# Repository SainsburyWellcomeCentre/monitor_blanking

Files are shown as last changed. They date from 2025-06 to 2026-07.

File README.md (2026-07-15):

# Monitor Blanking

A TTL-controlled light switch designed to blank monitor displays for use in behavioural experiments.

> **Note:** This device modifies existing monitors. Some tuning may be required depending on the model.

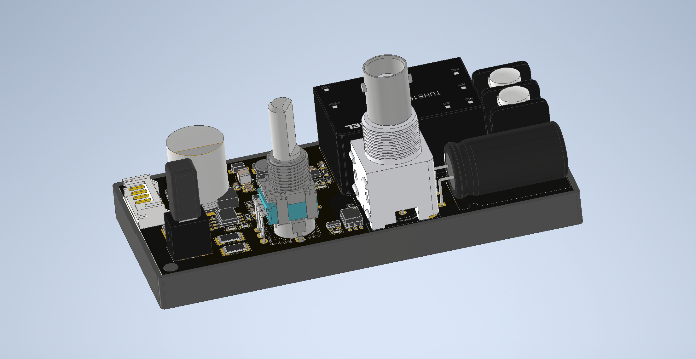
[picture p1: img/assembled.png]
Assembled


In systems neuroscience research, you want to present visual stimuli to animals without damaging the sensors you use to record neural activity. e.g. photomultiplier (PMT) for multiphoton imaging. Monitor blanking is a commonly used approach to minimize monitor light contamination by blanking the monitor backlight during the imaging pixel acquisition. The monitor turns on only during flyback periods of the fast-scan axis. Another approach is to use [a 3D-printed cone](https://labrigger.com/blog/2024/11/17/a-fantastic-shroud-for-visual-stimulation-during-imaging/).

## 🔧 Features

- Electrically isolated TTL input (up to 1 MHz)
- Sub-1 µs switching time
- Adjustable backlight brightness
- Forced-on switch for testing/debugging
- Supports up to 15 W output power

## 🌐 View Online (eCAD)

View the complete electronic design project online via [Altium 365 Viewer](https://sainsburywellcomecentre.github.io/fablabs-documentation/#fablabs-monitor-blanking).



## Build your own

Check out the **[latest release](https://github.com/SainsburyWellcomeCentre/fablabs-monitor-blanking/releases/latest)** for complete production files and instructions to build your own monitor blanking circuit.

## 🚀 Getting Started

Connect the monitor to your computer and adjust the resolution, scaling, etc. On Windows, navigate to `Settings > System > Display`. Pressing the **Forced ON** button will enable _debug_ mode, where the monitor functions as a standard monitor without digital pulses.

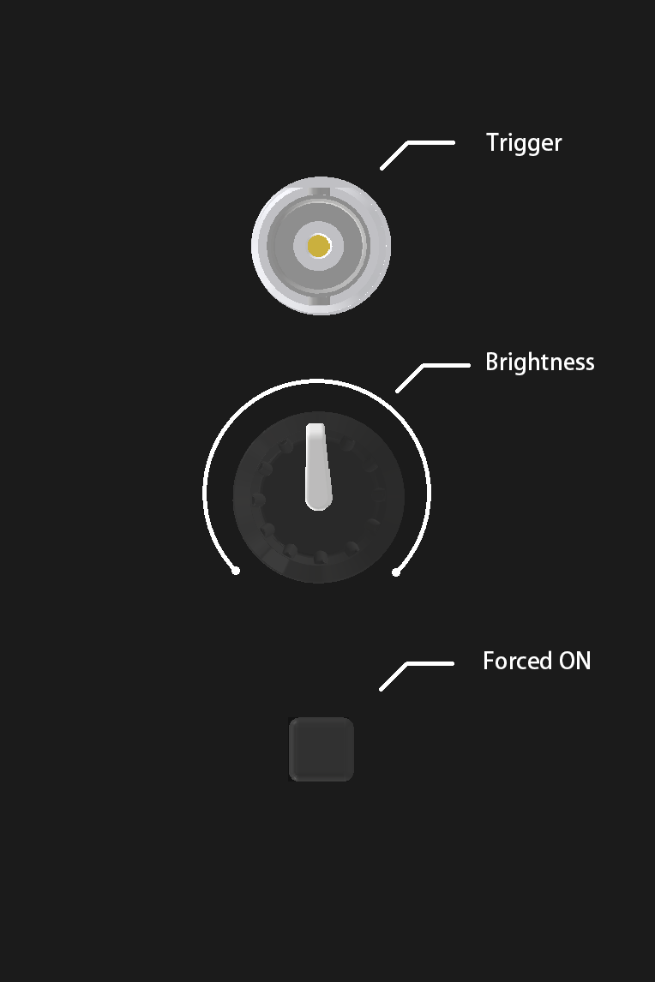
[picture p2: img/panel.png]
Panel


Once the monitor is detected and configured (also disable the _debug_ mode), send digital pulses from your fast-axis mirror through the **Trigger** BNC connection. A low signal will blank the monitor, and a high signal will allow backlight illumination. (hence, you cannot see anything if you are not sending TTL pulses.) Here are example functions for ScanImage users to generate and send monitor blanking TTLs. [BaselLaserMouse/ScanImageTools](https://github.com/BaselLaserMouse/ScanImageTools)

The luminance of the monitor can be measured using a luminance meter (e.g. LS-100, Konica Minolta) or a light sensor (e.g. Photodiode, Champalimaud Foundations’s Hardware Platform).

## ⚙️ Fine-Tuning the Blanking Driver

The blanking driver circuit is designed to support a wide range of monitor backlight types. However, to ensure optimal performance, you may need to fine-tune the **VLED** voltage.

### 🔧 Voltage Adjustment Guidelines

- Press the pushbutton to force the monitor **ON**, then use the trimmer **R9** to adjust the **VLED** until the backlight reaches the desired brightness level.
- The output voltage **VLED** can be adjusted within the range of **41 V to 61 V**.
  > The recommended **VLED** is at least **2 V higher** than the forward voltage of the backlight panel.

<div align="center">
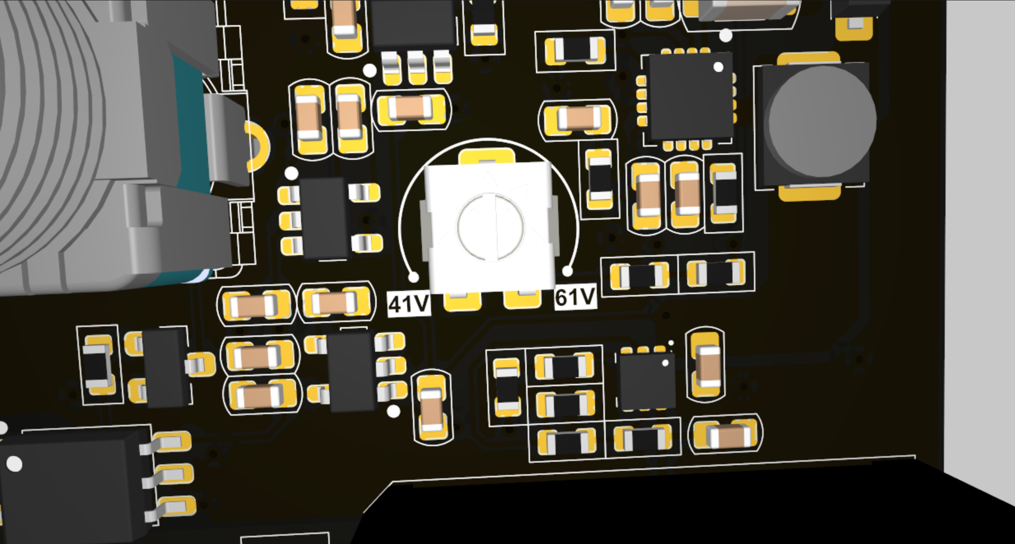
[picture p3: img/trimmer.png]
Trimmer R9
  
</div>

## 💻 Software Requirements

To access the source CAD projects:

- **Altium Designer 24** or newer  
  Academic licenses available via [Altium Education](https://www.altium.com/education/)
- **Autodesk Inventor Pro 2025** or newer  
  Academic licenses via [Autodesk Education](https://www.autodesk.com/education/home)

## 📜 License

**Sainsbury Wellcome Centre hardware is released under** [Creative Commons Attribution-ShareAlike 4.0 International](http://creativecommons.org/licenses/by-sa/4.0/).

You are free to:

- **Share** — copy and redistribute the material in any medium or format
- **Adapt** — remix, transform, and build upon the material for any purpose

Under the following terms:

- **Attribution** — Give appropriate credit, link to the license, and indicate changes.
- **ShareAlike** — Distribute your contributions under the same license.
- **No additional restrictions** — Don’t apply legal or technological measures that prevent others from doing anything the license permits.

> For the full legal text, see [LICENSE](LICENSE).

## 📚 Reference

```bibtex
@ARTICLE{Leinweber2014-nf,
  title     = "Two-photon calcium imaging in mice navigating a virtual reality environment",
  author    = "Leinweber, Marcus and Zmarz, Pawel and Buchmann, Peter and Argast, Paul and Hübener, Mark and Bonhoeffer, Tobias and Keller, Georg B",
  journal   = "Journal of visualized experiments: JoVE",
  number    =  84,
  pages     = "e50885",
  month     =  feb,
  year      =  2014,
  url       =  "https://app.jove.com/t/50885/two-photon-calcium-imaging-mice-navigating-virtual-reality",
  doi       =  {10.3791/50885}
}

```

## 🤝 Contributing

1. Fork the repository
2. Create a feature branch
3. Make your changes
4. Submit a pull request

## ❤ Contributors

 <a href = "https://github.com/sainsburywellcomecentre/fablabs-monitor-blanking/graphs/contributors">
   Contributors
 </a>

## 📧 Contact

- **Author**: [Sainsbury Wellcome Centre FabLabs](https://www.sainsburywellcome.org/content/fablab)
- **Email**: [swc.fablabs@ucl.ac.uk](mailto:swc.fablabs@ucl.ac.uk)
- **Website**: [FabLabs](https://sainsburywellcomecentre.github.io/fablabs-documentation/#fablabs-monitor-blanking)

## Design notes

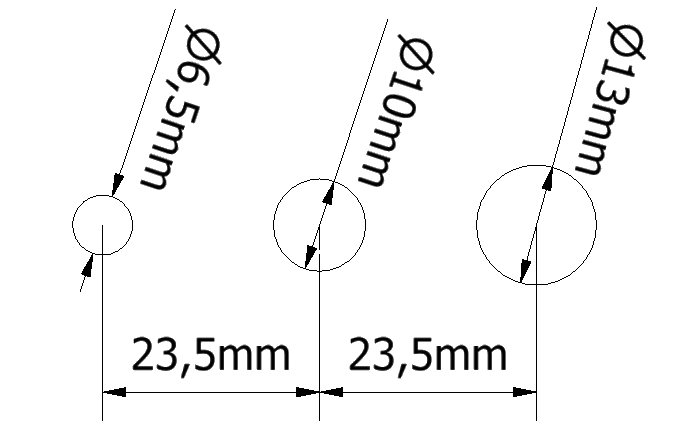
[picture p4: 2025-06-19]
img/drill.png

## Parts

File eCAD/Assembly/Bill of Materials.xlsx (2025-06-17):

Designator | Quantity | Value | PartNumber | Comment | Description | Footprint | LCSC Part N.
R9 | 1 | 1k | 3314J-1-102E | VR-SMD-1K-B | Trimmer, Cermet, 0.25W, 1000ohm, 300V, 20% +/-Tol, -100,100ppm/Cel, 1 Turn(s), 2018 | VR_SMD_4.5mm | C124640
U1 | 1 |  | TUHS15F12 | TUHS15F12 | AC/DC 15W 12V Single Output Power Supply, Encapsulated Board Mount Module | TUHS15F12 | C3031238
U7 | 1 |  | TPS70933DBVR | TPS70933 | LDO Regulator Pos 3.3V 0.15A 5-Pin SOT-23 T/R | SOT23-5 | C89347
U6 | 1 |  | TPS60403DBVR | TPS60403 | 60mA Charge Pump Voltage Inverter with Fixed 250kHz Operation 5-SOT-23 -40 to 85 | SOT23-5 | C11338
U4 | 1 |  | TPS25961DRVR | TPS25961 | 2.7-V–19-V, 106-mΩ, eFuse With Adjustable Current Limit and Short-Circuit | WSON6 | C5571272
U2 | 1 |  | TLP2361(TPL,E(T | TLP2361 | Logic IC Output Optocoupler, 1-Channel, 1-Element, 3750V Isolation, 20MBps | SO5 | C107626
U5 | 1 |  | SPX3819M5-L | SPX3819-ADJ | Adjustable Positive LDO Regulator, 0.7V Dropout, PDSO5 | SOT23-5 | C9056
R1 | 1 | 47R | RC2010FK-0747RL | R2010-47R | Res Thick Film 2010 47 Ohm 1% 3/4W ±100ppm/°C Molded SMD SMD Embossed T/R | RES_CHIP_2010 | C877463
R21 | 1 | 200mR | WSL2010R2000FEA18 | R2010-0R2 | Res Metal Strip 2010 0.2 Ohm 1% 1W ±75ppm/°C Molded SMD SMD Embossed Plastic T/R | RES_CHIP_2010 | C2073579
R4 | 1 | 470 | 0603WAF4700T5E | R0603-470R | 100mW Thick Film Resistors 75V ±100ppm/℃ ±1% 0603 Chip Resistor | RES_CHIP_0603 | C23179
R11 | 1 | 470k | 0603WAF4703T5E | R0603-470K | 100mW Thick Film Resistors 75V ±100ppm/℃ ±1% 0603 Chip Resistor | RES_CHIP_0603 | C23178
R16 | 1 | 390k | 0603WAF3903T5E | R0603-390K | 100mW Thick Film Resistors 75V ±100ppm/℃ ±1% 0603 Chip Resistor | RES_CHIP_0603 | C23150
R22 | 1 | 240k | AC0603DR-07240KL | R0603-240K | 100mW Thick Film Resistors 75V ±100ppm/℃ ±1% 0603 Chip Resistor | RES_CHIP_0603 | C227471
R5 | 1 | 120k | 0603WAF1203T5E | R0603-120K | 100mW Thick Film Resistors 75V ±100ppm/℃ ±1% 0603 Chip Resistor | RES_CHIP_0603 | C25808
R7 | 1 | 100k | 0603WAF1003T5E | R0603-100K | 100mW Thick Film Resistors 75V ±100ppm/℃ ±1% 0603 Chip Resistor | RES_CHIP_0603 | C25803
R15, R17 | 2 | 47k | 0603WAF4702T5E | R0603-47K | 100mW Thick Film Resistors 75V ±100ppm/℃ ±1% 0603 Chip Resistor | RES_CHIP_0603 | C25819
R12 | 1 | 39k | 0603WAF3902T5E | R0603-39K | 100mW Thick Film Resistors 75V ±100ppm/℃ ±1% 0603 Chip Resistor | RES_CHIP_0603 | C23153
R2, R8, R13, R23 | 4 | 10k | 0603WAF1002T5E | R0603-10K | 100mW Thick Film Resistors 75V ±100ppm/℃ ±1% 0603 Chip Resistor | RES_CHIP_0603 | C25804
R14 | 1 | 2.2k | 0603WAF2201T5E | R0603-2K2 | 100mW Thick Film Resistors 75V ±100ppm/℃ ±1% 0603 Chip Resistor | RES_CHIP_0603 | C4190
R6 | 1 | 2k | 0603WAF2001T5E | R0603-2K | 100mW Thick Film Resistors 75V ±100ppm/℃ ±1% 0603 Chip Resistor | RES_CHIP_0603 | C22975
R10, R18, R19, R20 | 4 | 1k | 0603WAF1001T5E | R0603-1K | 100mW Thick Film Resistors 75V ±100ppm/℃ ±1% 0603 Chip Resistor | RES_CHIP_0603 | C21190
D1 | 1 |  | PMEG10010ELRX | PMEG10010ELR | On a Reel of 3000, Nexperia 100V 1.4A, Schottky Diode, 2-Pin SOD-123W PMEG10010ELRX | SOD123 | C179426
U8 | 1 |  | OPA2197IDR | OPA2197 | 10MHz 5pA Dual channel SOIC-8 Precision Op Amps | SOIC8 | C139363
L1 | 1 | 10uH | SPM4015T-100M-LR | L-PWR-10uH-1.5A | Inductor Power Shielded Wirewound 10uH 20% 100KHz Metal 1.5A 0.345Ohm DCR T/R | IND_PWR_0404 | C695172
U3 | 1 |  | LM5158QRTERQ1 | LM5158 | 5-A, 40-V, wide VIN boost, flyback, & SEPIC converter 16-WQFN -40 to 150 | QFN16_3X3_0.5E_EP | C3188431
CN3 | 1 |  | 5227222-3 | LIGHT TRIGGER | RF BNC Connector, Female, Panel Mount, Board Mount, Solder Terminal, Jack | BNC-TE-5227222 | C3175614
SW1 | 1 |  | SPPH410100 | FORCE ON | Switch Push Button N.O./N.C. DPDT Plunger 0.1A 30VDC Latching PC Pins Thru-Hole Bulk | SW_LOCK_SPPH410100 | C370973
C3 | 1 | 220uF | EEEFK1J221AQ | EC125-220uF-63V | Radial Can - SMD ALUMINUM ELECTROLYTIC CAPACITOR FK 63V 220muF 20% 0.492Dia 12.50mm | ECAP_SMD_D12.5_13.5L | C215762
C2 | 1 | 33µF | 450BXW33MEFR12.5X25 | EC125-33uF-450V | Aluminum Electrolytic Capacitor, Polarized, Aluminum (wet), 450V, 20% +Tol, 20% -Tol, 33uF, Through Hole Mount | ECAP_DIP_12.5_90 | C1589601
C7 | 1 | 10uF | GRM32ER71J106KA12L | C1210-10uF-63V | Multilayer Ceramic Capacitors MLCC - SMD/SMT 1210 10uF 63volts *Derate Voltage/Temp | CAP_CHIP_1210 | C437568
C9 | 1 | 470pF | CC0603KRX7R8BB471 | C0603-470pF-25V | 25V 470pF X7R ±10% 0603 Multilayer Ceramic Capacitors MLCC - SMD/SMT ROHS | CAP_CHIP_0603 | C519413
C6 | 1 | 100nF | CC0603KRX7R0BB104 | C0603-100nF-100V | 0603 0.1 uF 100 V ±10% Tolerance X7R Multilayer Ceramic Capacitor | CAP_CHIP_0603 | C113803
C1, C8, C19, C21, C22 | 5 | 100nF | CC0603KRX7R9BB104 | C0603-100nF-50V | 0603 Multilayer Ceramic Capacitors MLCC | CAP_CHIP_0603 | C14663
C10 | 1 | 33nF | CL10B333KB8NNNC | C0603-33nF-50V | 0603 Multilayer Ceramic Capacitors MLCC | CAP_CHIP_0603 | C21117
C11, C13, C14 | 3 | 10µF | CL10A106MA8NRNC | C0603-10uF-25V | 0603 Multilayer Ceramic Capacitors MLCC | CAP_CHIP_0603 | C96446
C20 | 1 | 10nF | 0603B103K500NT | C0603-10nF-50V | 0603 Multilayer Ceramic Capacitors MLCC | CAP_CHIP_0603 | DNP
C4, C5, C12, C15, C16, C17, C18 | 7 | 1µF | CL10A105KB8NNNC | C0603-1uF-50V | 0603 Multilayer Ceramic Capacitors MLCC | CAP_CHIP_0603 | C15849
Q1 | 1 |  | BSC070N10NS5 | BSC070N10NS5 | MOSFET Power-Transistor, 100V / Superior thermal resistance | TDSON-8 | C534364
R3 | 1 | 10k | RK09L114001T | BRIGHTNESS | Potentiometer, 0.05W, 10000ohm, 10V, 20% +/-Tol, 1 Turn(s), 4845 | RK09L1140 | C470463
CN2 | 1 |  | X2016WR-06-46SN | BACKLIGHT PANEL | Wire-To-Board Connector, Right Angle, 2 mm, 2 Contacts, Header, PH Series | PH_DIP_90_1X6P | C696999
Q2 | 1 |  | AO3400A | AO3400A | 30V 5.7A 26.5mΩ@10V,5.7A 1.4W 1.5V@250uA 1 NChannel SOT-23-3L MOSFETs | SOT23 | C20917
CN1 | 1 |  | 4DB-P108-02 | AC IN | CONN BARRIER STRIP 2CIRC 0.325" | BT-8.26-1X2P | C5902324

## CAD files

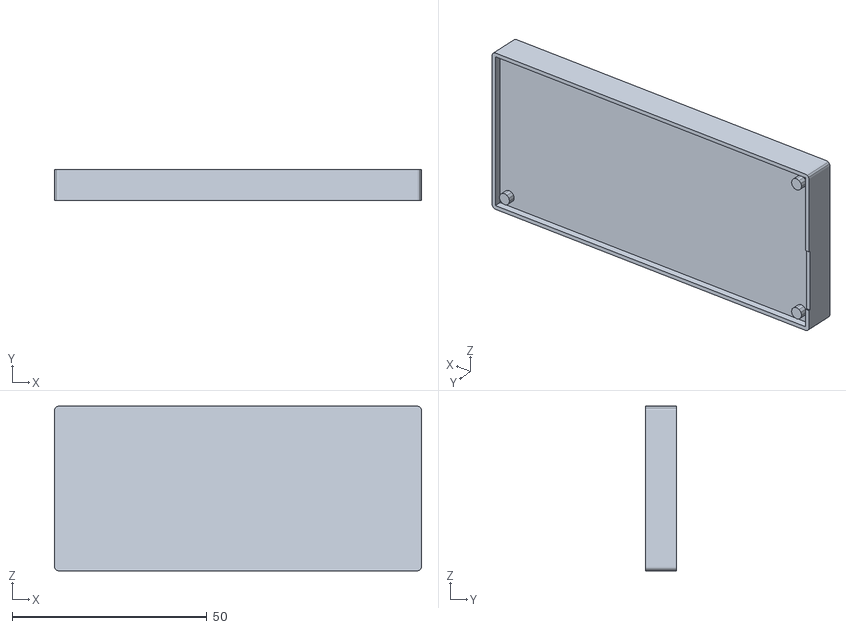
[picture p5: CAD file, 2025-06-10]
MCAD/3DP/base.stl
94.3 x 8.00 x 42.3

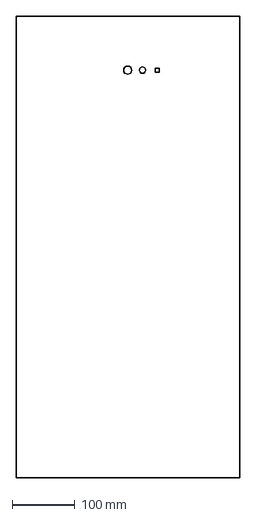
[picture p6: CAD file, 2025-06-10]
MCAD/panel_drill.dxf
354.7 x 732.7 mm

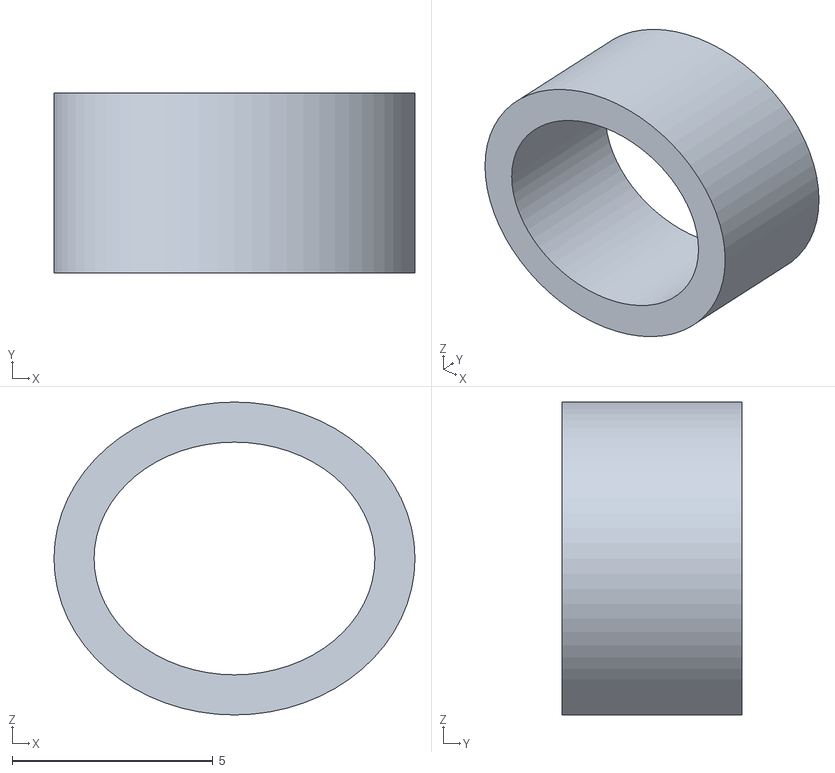
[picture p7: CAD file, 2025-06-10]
MCAD/3DP/RING.stl
9.00 x 4.50 x 7.80

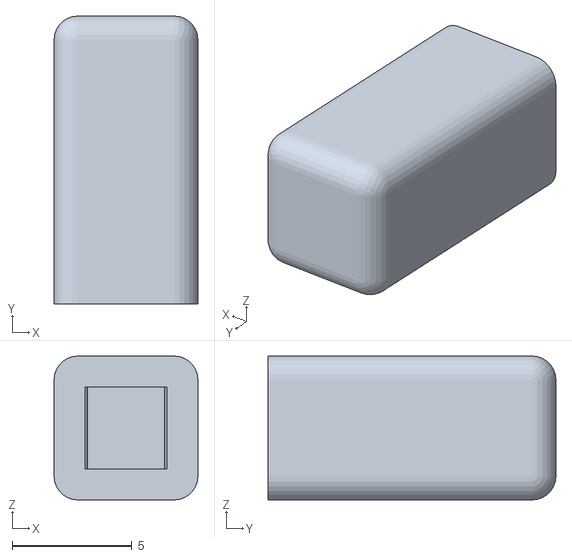
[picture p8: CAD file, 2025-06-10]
MCAD/3DP/Button.stl
6.00 x 12.0 x 6.00

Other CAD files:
MCAD/Source/Button.ipt
MCAD/Source/PCBA/ConvertedComponents/BNC-TE-5227222_CMP-730-0010-3.ipt
MCAD/Source/PCBA/ConvertedComponents/BT-8.26-1X2P_CMP-330-0001-1.ipt
MCAD/Source/PCBA/ConvertedComponents/CAP_CHIP_0603_CMP-611-0022-7.ipt
MCAD/Source/PCBA/ConvertedComponents/CAP_CHIP_0603_CMP-611-0027-24.ipt
MCAD/Source/PCBA/ConvertedComponents/CAP_CHIP_0603_CMP-611-0033-11.ipt
MCAD/Source/PCBA/ConvertedComponents/CAP_CHIP_0603_CMP-611-0050-6.ipt
MCAD/Source/PCBA/ConvertedComponents/CAP_CHIP_0603_CMP-611-0076-2.ipt
MCAD/Source/PCBA/ConvertedComponents/CAP_CHIP_0603_CMP-611-0085-1.ipt
MCAD/Source/PCBA/ConvertedComponents/CAP_CHIP_0603_CMP-611-0088-1.ipt
MCAD/Source/PCBA/ConvertedComponents/CAP_CHIP_1210_CMP-611-0087-1.ipt
MCAD/Source/PCBA/ConvertedComponents/ECAP_DIP_12.5_90_CMP-612-0013-1.ipt
MCAD/Source/PCBA/ConvertedComponents/ECAP_SMD_D12.5_13.5L_CMP-612-0011-1.ipt
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

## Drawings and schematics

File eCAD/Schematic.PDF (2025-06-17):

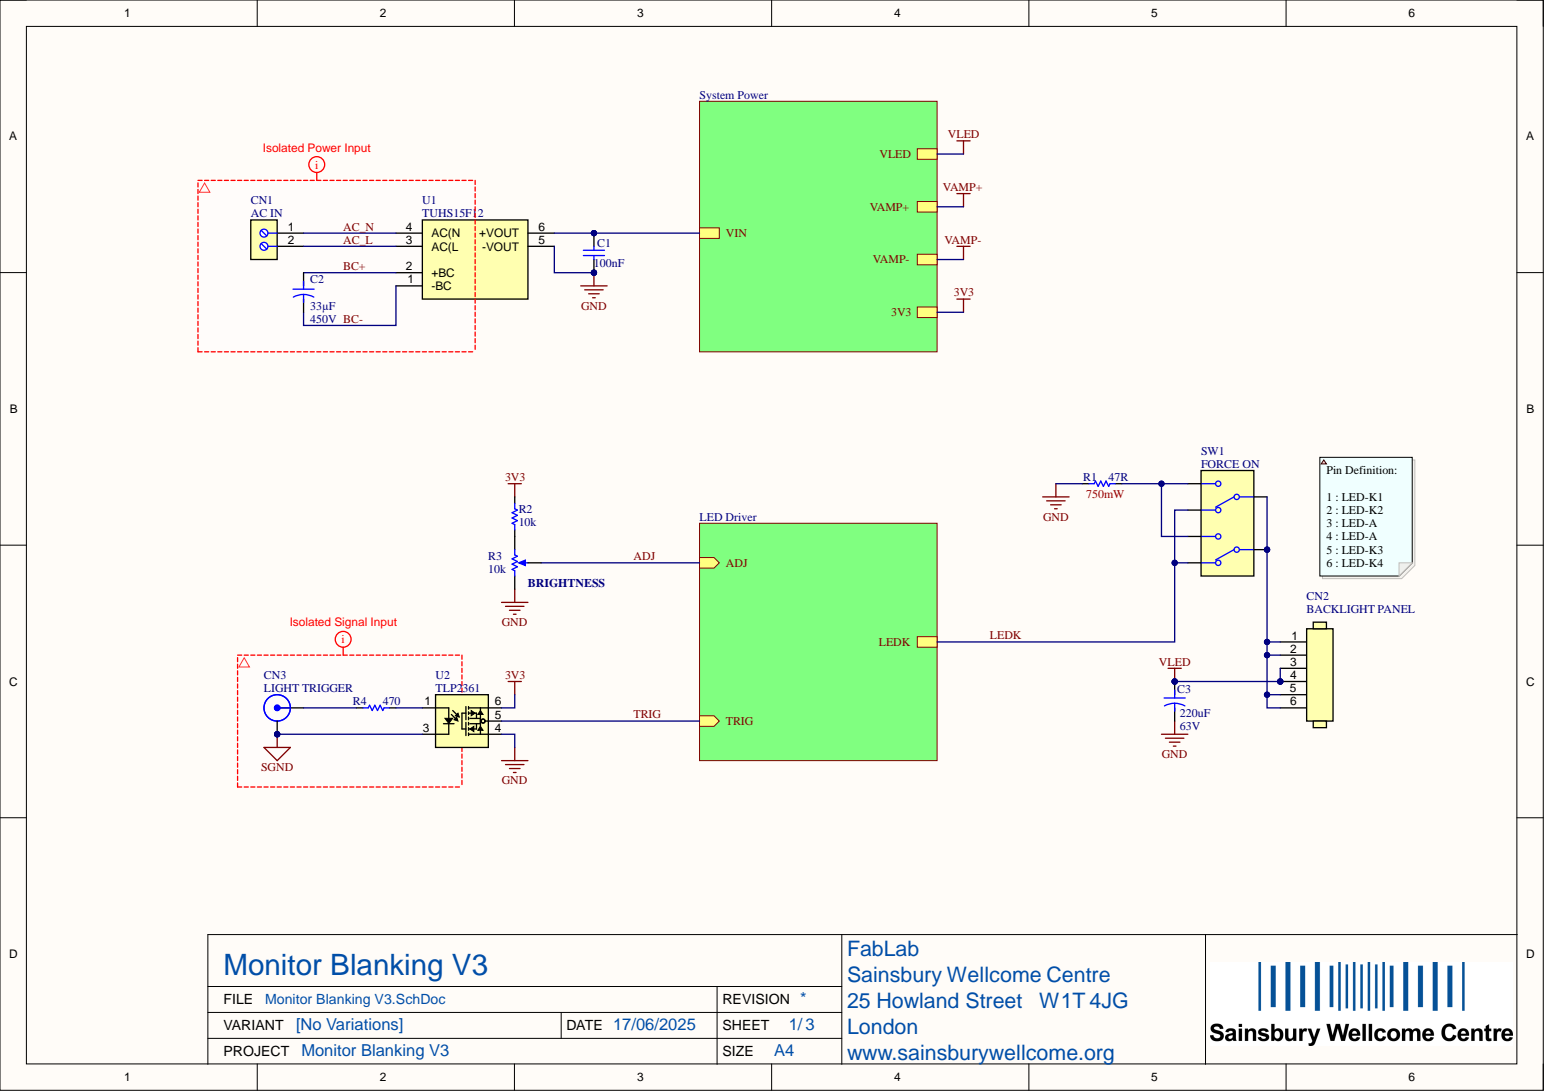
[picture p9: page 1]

FILE Monitor Blanking V3.SchDoc | * REVISION

PROJECT Monitor Blanking V3 VARIANT [No Variations]

DATE | SHEET 1 / 3

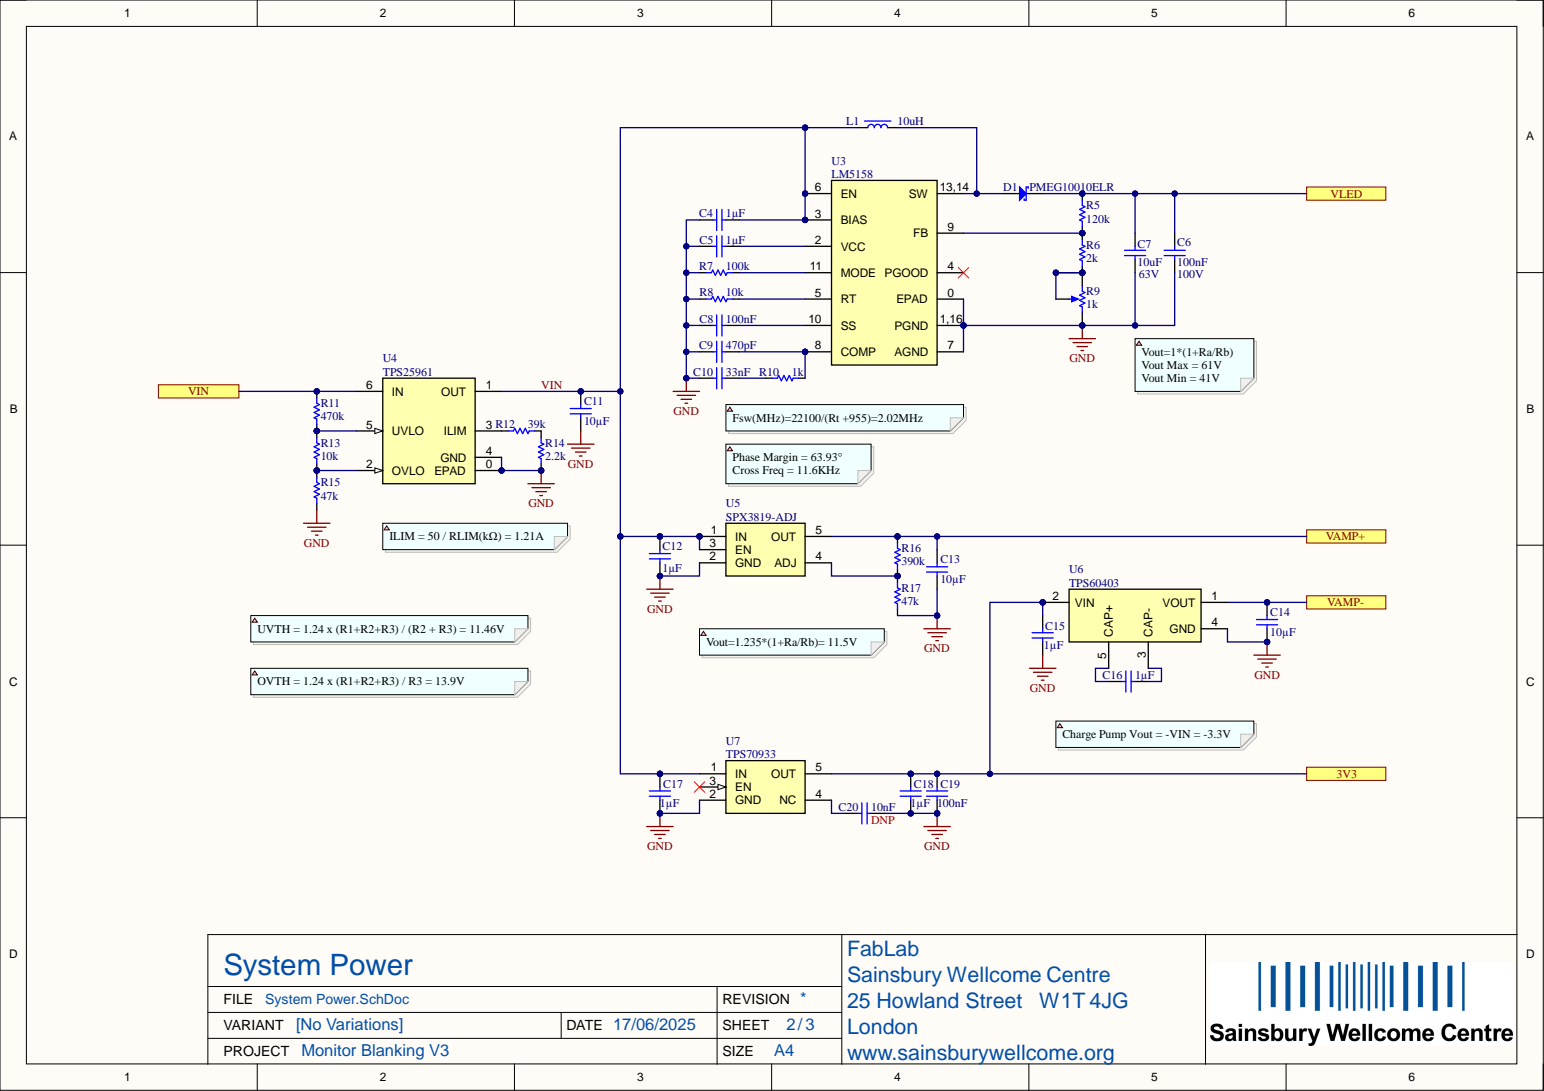
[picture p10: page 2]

Vout=1*(1+Ra/Rb) Vout Max = 61V Vout Min = 41V

Charge Pump Vout = -VIN = -3.3V

FILE System Power.SchDoc | * REVISION

PROJECT Monitor Blanking V3 VARIANT [No Variations]

SHEET 2 / 3

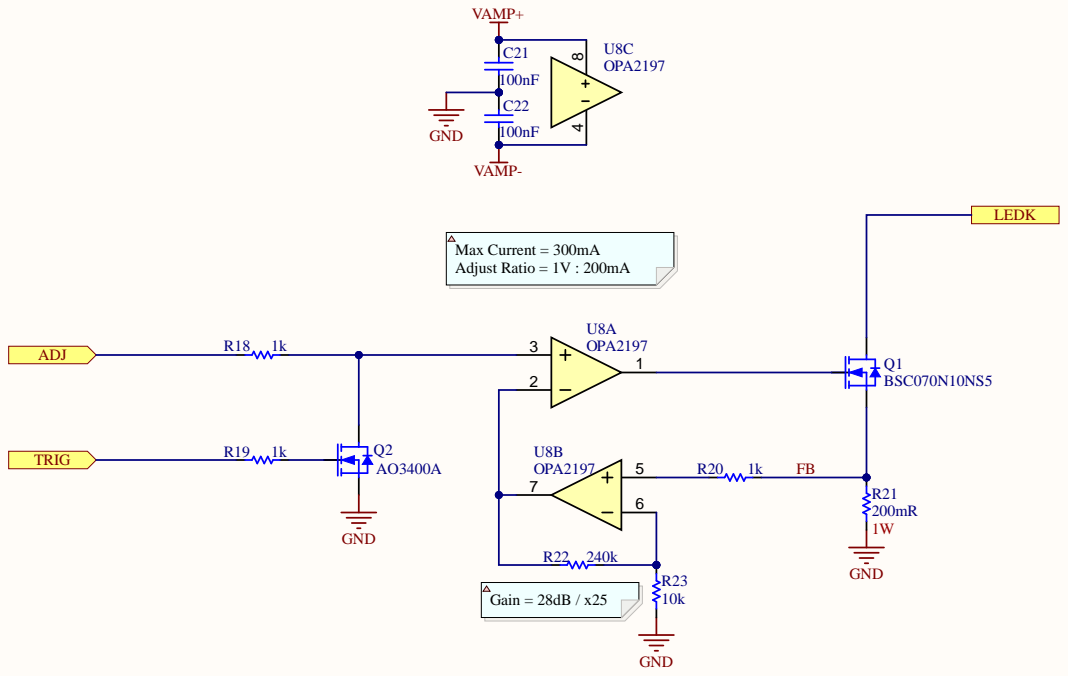
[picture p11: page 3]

FILE LED Driver.SchDoc | * REVISION

PROJECT Monitor Blanking V3 VARIANT [No Variations]

SHEET 3 / 3

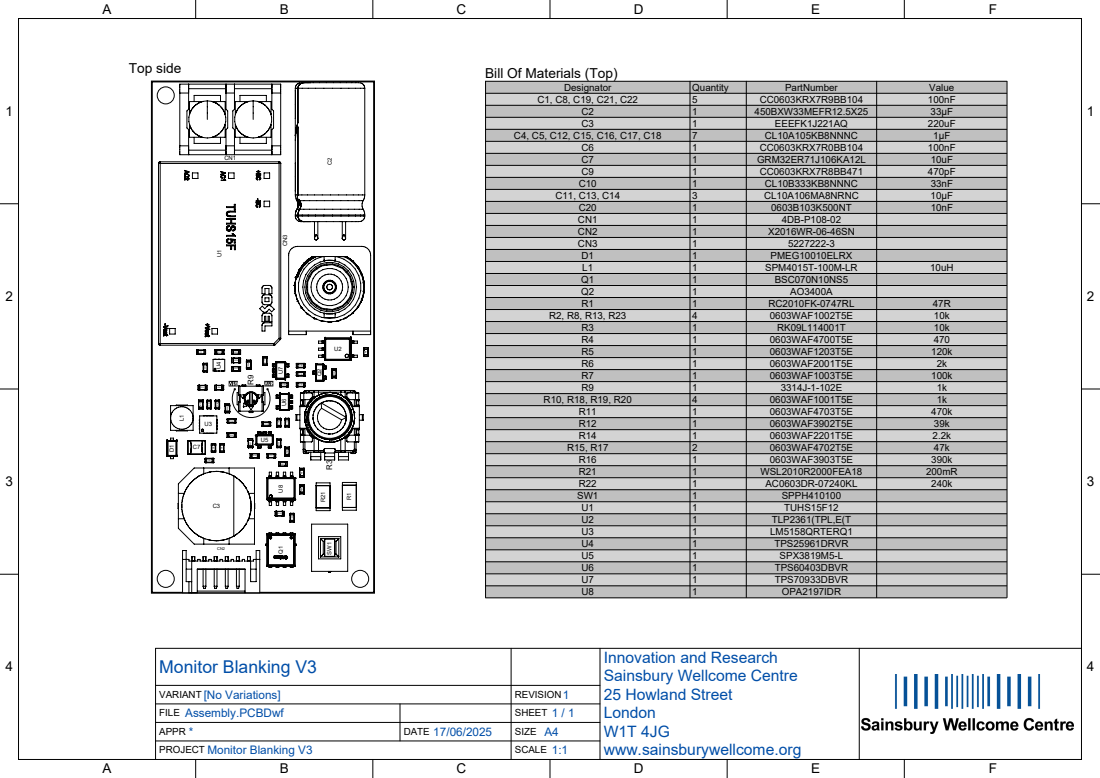
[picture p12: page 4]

Bill Of Materials (Top)

Designator | Quantity | PartNumber | Value
C1, C8, C19, C21, C22 | 5 | CC0603KRX7R9BB104 | 100nF

C2 | 1 | 450BXW33MEFR12.5X25 | 33µF
C3 | 1 | EEEFK1J221AQ | 220uF

C4, C5, C12, C15, C16, C17, C18 | 7 | CL10A105KB8NNNC | 1µF

C6 | 1 | CC0603KRX7R0BB104 | 100nF

C9 | 1 | CC0603KRX7R8BB471 | 470pF
C10 | 1 | CL10B333KB8NNNC | 33nF
C11, C13, C14 | 3 | CL10A106MA8NRNC | 10µF
C20 | 1 | 0603B103K500NT | 10nF
CN1 | 1 | 4DB-P108-02
CN2 | 1 | X2016WR-06-46SN
CN3 | 1 | 5227222-3
D1 | 1 | PMEG10010ELRX
L1 | 1 | SPM4015T-100M-LR | 10uH
Q1 | 1 | BSC070N10NS5
Q2 | 1 | AO3400A
R1 | 1 | RC2010FK-0747RL | 47R
R2, R8, R13, R23 | 4 | 0603WAF1002T5E | 10k
R3 | 1 | RK09L114001T | 10k
R4 | 1 | 0603WAF4700T5E | 470
R5 | 1 | 0603WAF1203T5E | 120k
R6 | 1 | 0603WAF2001T5E | 2k
R7 | 1 | 0603WAF1003T5E | 100k
R9 | 1 | 3314J-1-102E | 1k

R10, R18, R19, R20 | 4 | 0603WAF1001T5E | 1k

R11 | 1 | 0603WAF4703T5E | 470k
R12 | 1 | 0603WAF3902T5E | 39k
R14 | 1 | 0603WAF2201T5E | 2.2k
R15, R17 | 2 | 0603WAF4702T5E | 47k
R16 | 1 | 0603WAF3903T5E | 390k
R21 | 1 | WSL2010R2000FEA18 | 200mR
R22 | 1 | AC0603DR-07240KL | 240k
SW1 | 1 | SPPH410100
U1 | 1 | TUHS15F12
U2 | 1 | TLP2361(TPL,E(T
U3 | 1 | LM5158QRTERQ1
U4 | 1 | TPS25961DRVR
U5 | 1 | SPX3819M5-L
U6 | 1 | TPS60403DBVR
U7 | 1 | TPS70933DBVR
U8 | 1 | OPA2197IDR

[No Variations] VARIANT | 1 REVISION
FILE Assembly.PCBDwf | | SHEET 1 / 1
APPR *

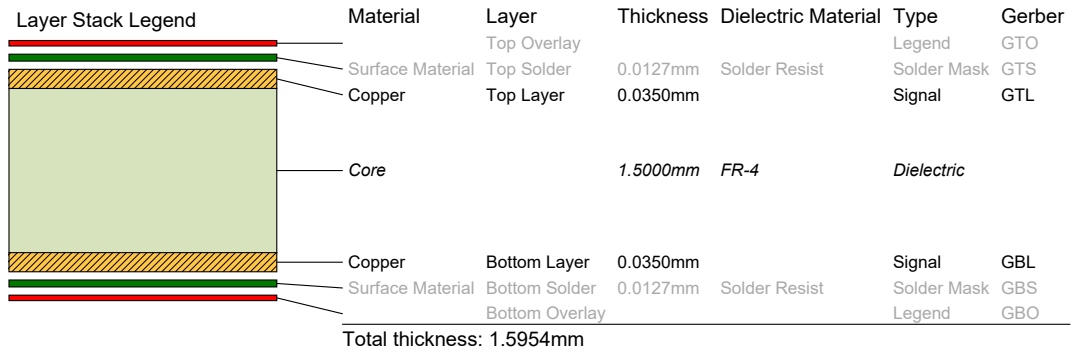
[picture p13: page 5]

[No Variations] VARIANT | 1 REVISION
FILE Fabrication.PCBDwf | | SHEET 1 / 2
APPR *

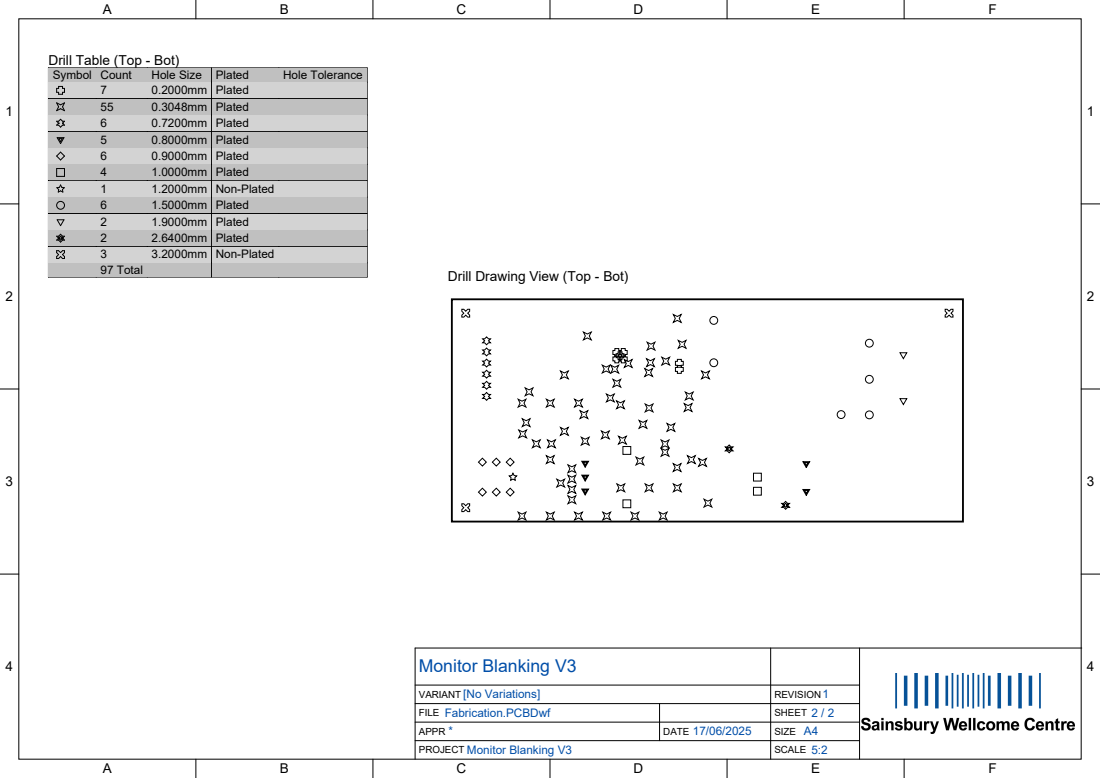
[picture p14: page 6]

Drill Table (Top - Bot)

Symbol | Count | Hole Size | Plated | Hole Tolerance

7 | 0.2000mm | Plated
55 | 0.3048mm | Plated
6 | 0.7200mm | Plated
5 | 0.8000mm | Plated
6 | 0.9000mm | Plated
4 | 1.0000mm | Plated
1 | 1.2000mm | Non-Plated
6 | 1.5000mm | Plated
2 | 1.9000mm | Plated
2 | 2.6400mm | Plated
3 | 3.2000mm | Non-Plated
97 Total

Drill Drawing View (Top - Bot)

[No Variations] VARIANT | 1 REVISION
FILE Fabrication.PCBDwf | | SHEET 2 / 2
APPR *

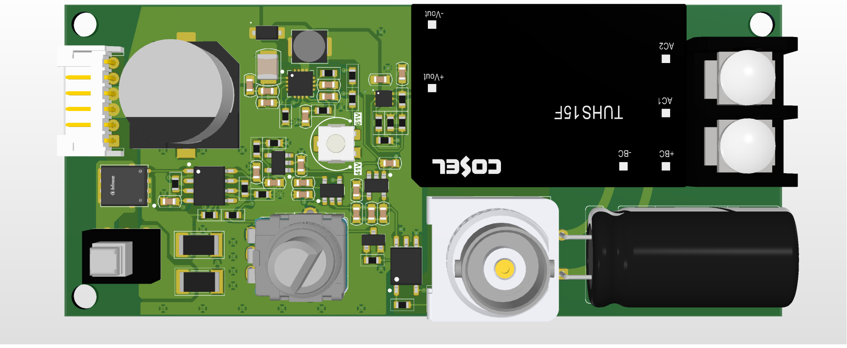
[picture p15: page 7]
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

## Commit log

2025-06-16 update readme and folder structure
    [Bill of Materials.xlsx, Generates pick and place files.csv, LED Driver.SchDoc, Monitor Blanking V3.GBL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]
2025-06-17 add vout adjustments
    [Bill of Materials.xlsx, Generates pick and place files.csv, Monitor Blanking V3.GBL, Monitor Blanking V3.GBO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]
2025-06-18 add drill img
